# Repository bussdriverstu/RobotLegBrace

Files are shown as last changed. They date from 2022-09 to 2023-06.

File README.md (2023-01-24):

# Robotic Leg Brace
A brace to assist someone with partial paralysis to bend their knee using off-the-shelf parts. Start with 'LegV2' directory.

## Intro Video:
Video Link (https://www.youtube.com/watch?v=BwBtS2pidzo)  
[click to play](https://www.youtube.com/watch?v=BwBtS2pidzo)

## FAQs
### What plans do you have in the future for this project?
~~I have some ideas for reintegrating the muscle sensors back into the leg to have more accurate bend timings.~~ UPDATE: Muscle sensors have been reintegrated, special thanks to [ANR Corp](https://www.anrcorp.com/) for their muscle sensors. I'd also like to program different gait modes for different terrain (hiking, uneven ground, etc).

### How long did this take?
I started the fall of 2021 after being ghosted by a company in San Franscico that makes warehouse exoskeletons. They wanted to expand into the medical field and I volunteered to be a guinea pig. After a few conversations with the CEO I never heard from them again. I assume I lived too far away to make this feasible and they found better candidates. It took me a few months before I started testing it on myself, a little over a year to get it to the point where I could hike with it.

### What is your injury and why is it so difficult to find a therapy?
I had a tumor in my spinal cord. Because it wasn't the result of a tramatic injury, therapies like stem cells are riskier for me. I assume this is because they'd rather avoid growing another tumor, but I don't know. In addition, most robot knee assist devices out there target people who can't hold their weight with their leg, i.e. they can bend but can not straighten their leg. e.g. [The C Brace is one of these devices that I had a consultation with.](https://www.ottobock.com/en-us/c-brace). I have the opposite problem and haven't been able to find a solution so far. After years of frustration, I just decided to try to build my own.

### Why don't you patent this or sell it?
I believe in universal healthcare and have suffered from the ill-effects of for-profit healthcare for a long time. Anyone who has fought with insurance knows the phrase "medically necessary" all too well. Maybe I'm bitter, but I'd rather help people like me for free than join the profit model. Besides, this thing is jank; No one should build it let alone buy it. It works for me and that's good enough. I posted it here in case anyone out there wants to improve it or adapt it for their own needs. That said, you can donate to me or buy me a cup of coffee via bitcoin/ethereum here:  
Bitcoin Address: 36wiXyfY1boAd6eBREEssyqCdySTDvTCo1   
Ethereum Address: 0xE7dC5e4DE2950B2e13B2A2148E09333C0acBa920

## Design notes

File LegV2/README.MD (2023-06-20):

# Robot Leg Brace v2
## Introduction/Warning

Hi. I’ve been handicapped for about 9 years now, I’ve tried to seek out treatments to be able to walk again. However, because of the type of injury and the specific motion I’ve regained, there aren’t many options out there, especially for someone on a fixed income. I took it upon myself to build my own solution. I am not an engineer nor am I a programmer. **I do not recommend anyone follow in my footsteps. THIS IS DANGEROUS.** You could blow yourself up or injure yourself doing what I did. That said, I can walk without my crutch or cane again, which is all I wanted to do. I figured I’d share my project in case anyone else, who is poor and disabled like I am, wants to try to build their own solution. 

## Injury and Ability

My injury is unique and so my solution may not apply to you. I have full motion of my left leg; I can also straighten my right leg out and (mostly) hold my weight with it. The issue I have is being able to bend it back in after pushing it out. I also have foot drop, but I can point my toes easily enough. Again, it’s the bringing my foot back that is the issue. This device will detect when I want to bend my leg and do it for me.

## The Device

The device uses a knee brace as a base. I’ve attached a large servo to the outer thigh portion of the brace and used an old cut-up AFO foot brace to add rigidity to the two sides. I had a friend use a 3D printer to create a pulley to attach to the servo. A chain threaded through a spring which is wrapped around the servo wheel and attaches to the shin portion of the brace via another spring (this is to absorb shock of occasional muscle spasms I can have when my leg moves or is tired). When the servo rotates, it pulls the shin up, bending the knee. 

To control the servo, a microcontroller reads input from various sensors and/or a user-held button and determines when to move, bending or straightening the leg. For example, in Gait/Accelerometer mode, the microcontroller reads data from an accelerometer to determine where my leg is positioned during the walking gait. When the user's thigh reaches a certain angle, it will tell the servo to move, bending my leg. As the user moves forward, the angle will change and the servo will reverse direction, straighten the leg again. See the "Operations" section for more details and controls.

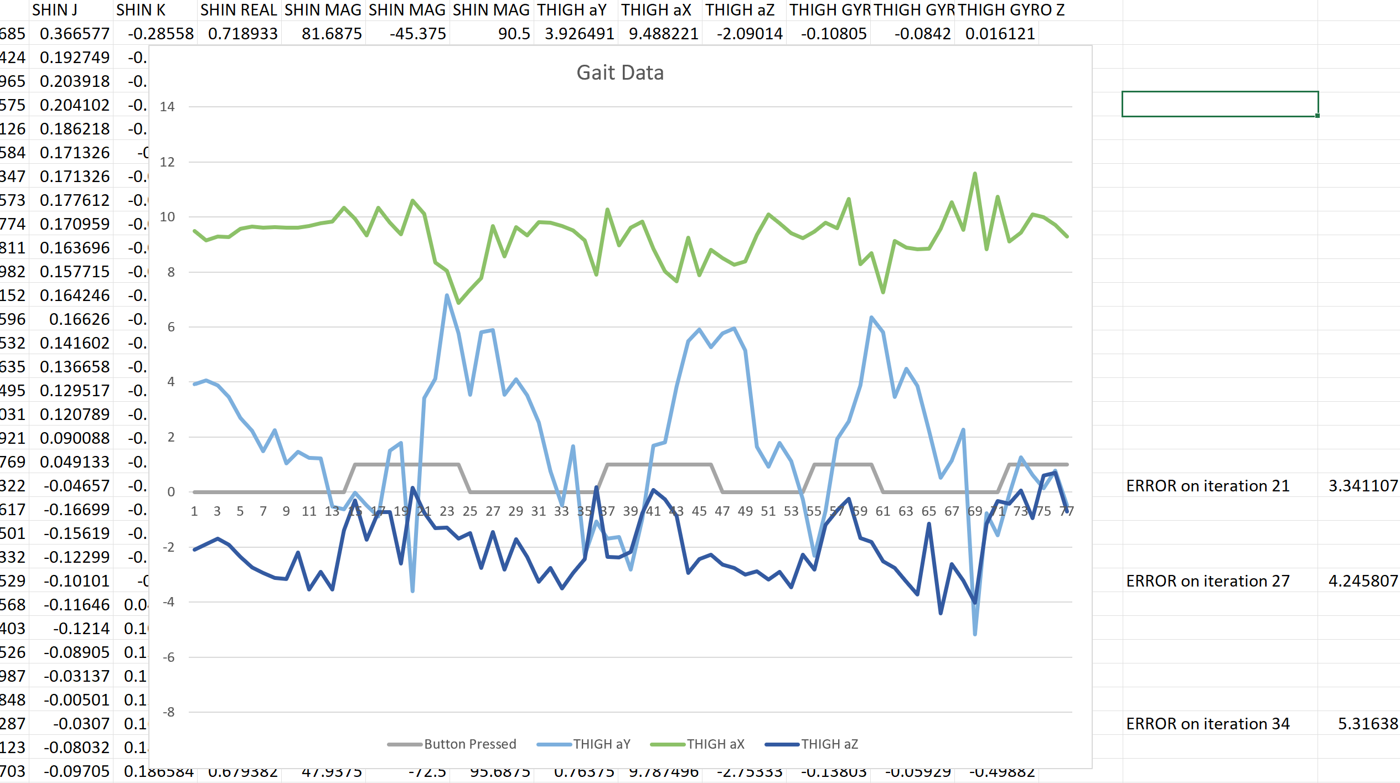
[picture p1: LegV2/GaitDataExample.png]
Gait Data


## Operation

There are a few controls to operate the device. A slider, a hand-held button, and the microcontroller's on-board button. Each have different functions depending on what operating mode the device is in.

### Manual Mode

When the potentiometer slider is at the zero-position (which side that is depends on how you've mounted it) press the handheld button to bend the knee, release to straighten it. When your leg is straight, the on-board LED will be green.

### Gait/Accelerometer Mode

In gait detection mode, the potentiometer slider will set the angle-position threshold that tells the servo when in the walking gait to begin bending the leg and when to straighten it again. A handheld momentary push button is used to override the sensors and manually bend the leg brace. This is useful for steps or uneven ground. You can operate the device in full manual mode by moving the slider all the way to one side (which side depends on how you’ve mounted it, but it will be refered to as the zero-position). An on-board LED light provides visual feedback of what state the brace is in. Green means the leg should be straight, red means the knee should be bent. 

### Muscle Activity Mode

There is an on-board button that will toggle operation from using the brace's position to bend to the muscle sensor. When using the muscle sensor, the light will change from green to blue and the position of the device will not affect bending and straightening. Flexing of the muscle the sensor is positioned on will bend the knee relative to how hard to flex. The slider adjusts the sensitivity of the muscle sensor so that you can get a strong signal from weak muscles. The manual bending button has also been reversed so that when you press it the leg will straighten. This was done as a safety precaution in case interference causes the muscle sensor to report higher readings than the muscle is sending. At rest, the on-board LED will be blue instead of green.

### Hybrid Mode

This mode allows for muscle activity to control the knee only when the leg is positioned within a certain threshold. When enabled it will force the leg to straighten when the leg swings forward past the set threshold. To enable, set the device in Manaul Mode by moving slider all the way to the zero-position in Gait Mode (On-board LED should be green) and use the bend-button to walk. The program will record the position of your leg when you first let go of the button to straighten during each step. Then, switch to muscle activity mode (On-board LED will be blue) and it will straighten your leg at the same position you released the button during the previous step, regardless of the muscle activity registered. To disable this feature, go to Gait mode (press the on-board button so the on-board LED is green and move the slider to any position other than zero) then press and release the bend button again. A white flash will indicate when you have enabled and set, or disabled the setting successfully.

## Installation, Code and Libraries

The code is written in CircuitPython 7.3 and uses the following libraries in the lib folder:

- adafruit_bno08x
- adafruit_bus_device
- adafruit_motor
- adafruit_seesaw
- adafruit_pixelbuf.mpy
- neopixel.mpy

Instructions for installing CircuitPython on the microcontroller can be found here: https://learn.adafruit.com/welcome-to-circuitpython/installing-circuitpython 

After installing, you should be able to copy 'code.py' and the entire 'lib' folder from this repository into the root directory of the microcontroller and you'll be done. Again, I am not a programmer, but I commented what most of it does to the best of my ability. 

## Design/Wiring Diagram

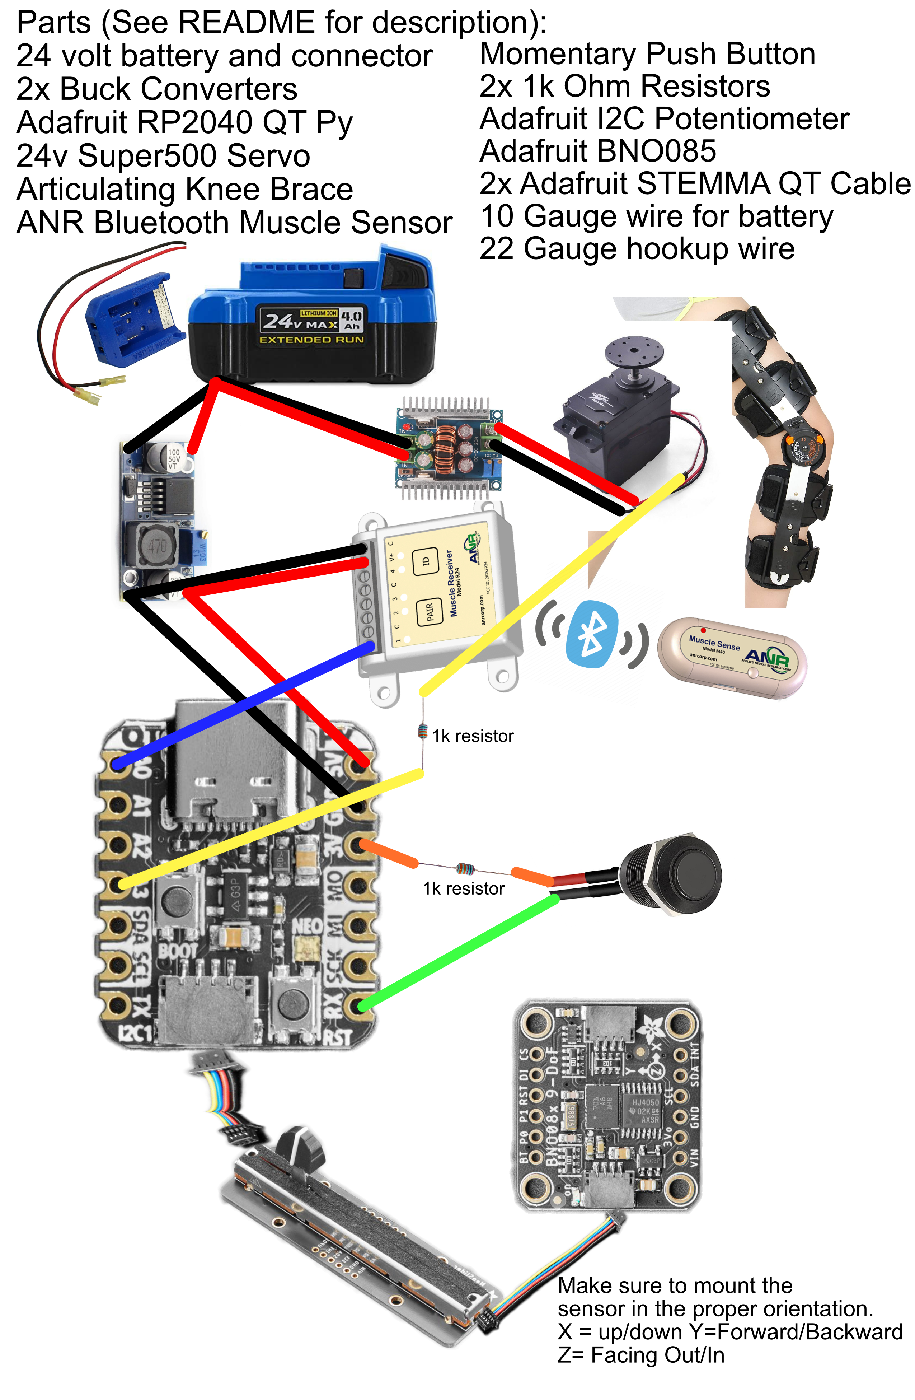
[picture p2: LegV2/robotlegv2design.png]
LegV2 Diagram


## Materials List for building Robot Leg Brace Version 2

- Brace https://www.amazon.com/gp/product/B07BT59Q6X
- Battery https://www.amazon.com/24-VOLT-4-0-AMP-LITHIUM-KB-424-03/dp/B01KAL4IO2
- Battery Quick Connect Terminal Adapter https://www.amazon.com/gp/product/B09BKGX81V
- Small Buck Converter https://www.amazon.com/gp/product/B07MKQXNWG/
- Large Buck Converter https://www.amazon.com/dp/B08GCX2RJ1
- Servo https://www.ebay.com/itm/123414770402
- 10 Gauge Wire https://www.amazon.com/Copper-American-Gauge-Wire/dp/B0796JJHTQ/
- 22 Gauge Wire https://www.amazon.com/Gauge-Wire-Solid-Hookup-Wires/dp/B088KQFHV7/
- Adafruit QT Py RP2040 https://www.adafruit.com/product/4900
- Adafruit BNO085 9-DOF Orientation Sensor https://www.adafruit.com/product/4754
- STEMMA QT Cable https://www.adafruit.com/product/4399
- 1k Ohm Resistors https://www.amazon.com/MCIGICM-Values-Resistor-Assortment-Resistors/dp/B06WRQS97C/
- ANR Corp R24 Muscle Receiver https://www.anrcorp.com/product/r24-muscle-receiver/
- ANR Corp Wireless Muscle Sensor M40 https://www.anrcorp.com/product/m40-muscle-sense/

## Notes

The original design used a Raspberry Pi Zero, input/output controls, a screen, and muscle sensors. It was written in Python 3.7 using multiple libraries from adafruit, waveshare, and users on github. I will upload that version at some point as it was useful for gathering data in my walking gait and experimenting with different techniques for detecting when to bend the leg brace. For now, this is a simplified version targeted toward walking on even ground and can be built with minimal soldering and programming experience.

Once you have the device working, the next challenge will be to fit it on your leg without it moving around. A tight, secure fit is needed to ensure the brace moves your leg instead of moving *on* your leg. I attached the lower portion of the brace directly to my foot drop AFO but still have trouble with the thigh piece sliding around. You will have to experiment on your own to get it right. Good luck.

## Update 2023

Thanks to [ANR Corp](https://www.anrcorp.com/) sending me their muscle sensors and design help from their president, I was able to succesfully integrate muscle sensors into the latest design of the robotic leg. See the operation section for more information on how they operate. ~~I may experiement with more than one muscle sensor in the future.~~ I've started using two sensors, one on the good leg and one on the disabled one. This gives a better picture of my gait so that the brace can respond appropriately. How a short demo of the muscle sensor, watch this video: [https://youtu.be/r48ZZ4WN5bA](https://youtu.be/r48ZZ4WN5bA)

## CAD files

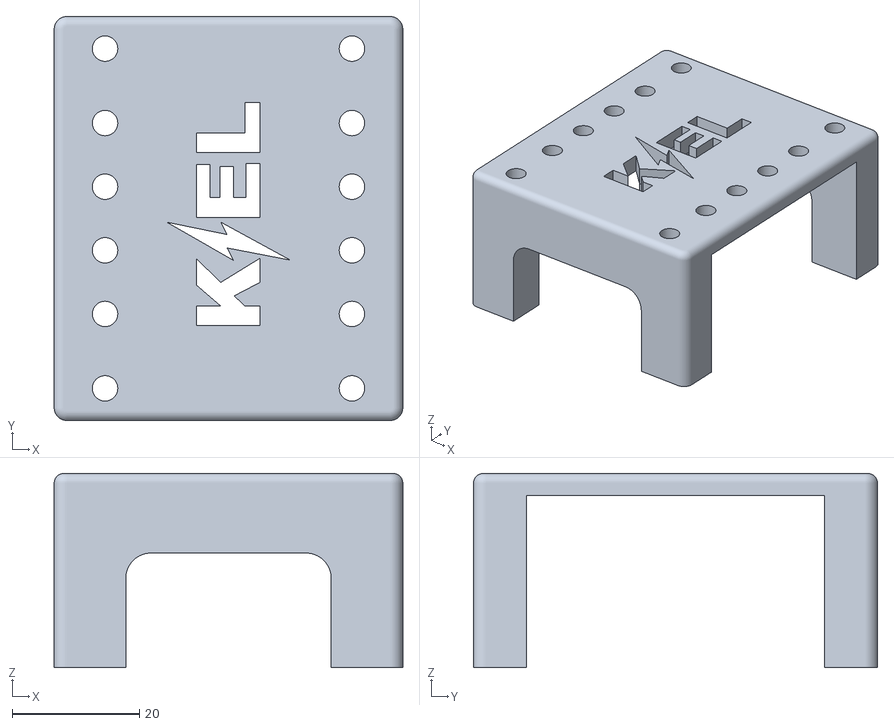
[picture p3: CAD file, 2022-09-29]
3D Printed Parts Files/power-convert-case-top.stl
54.8 x 63.5 x 30.5

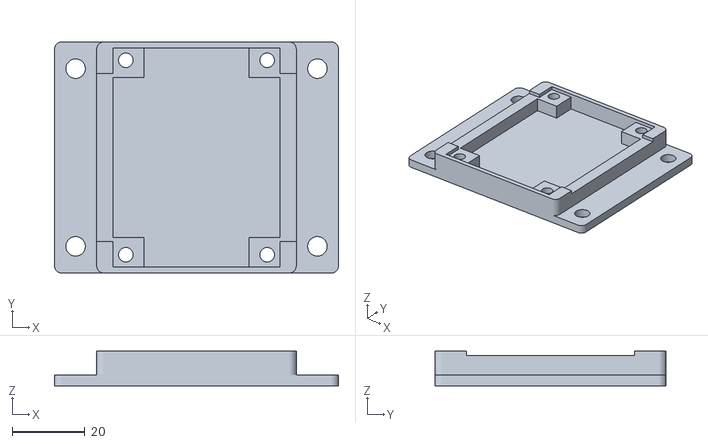
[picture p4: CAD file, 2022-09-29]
3D Printed Parts Files/power-convert-case-btm.stl
78.0 x 63.5 x 9.50

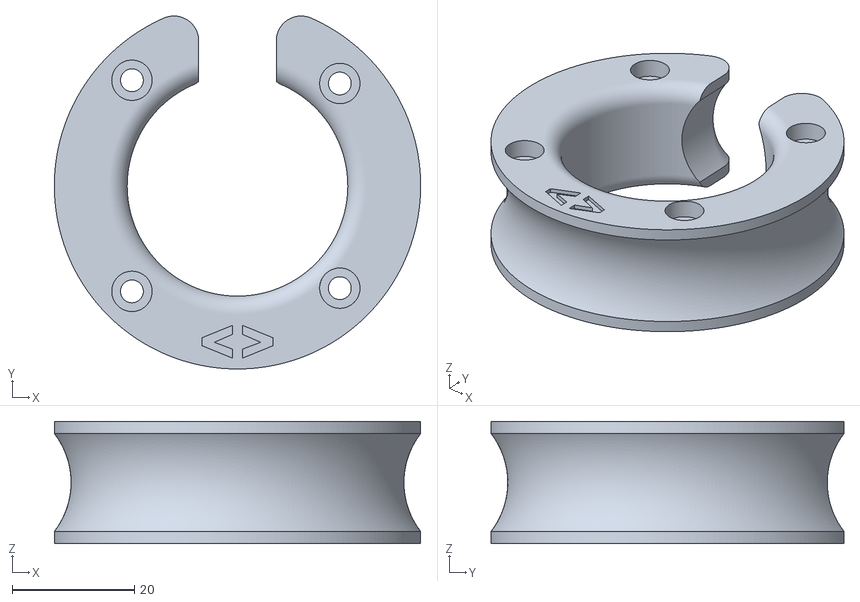
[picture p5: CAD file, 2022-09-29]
3D Printed Parts Files/spring-guide.stl
60.0 x 57.8 x 20.0

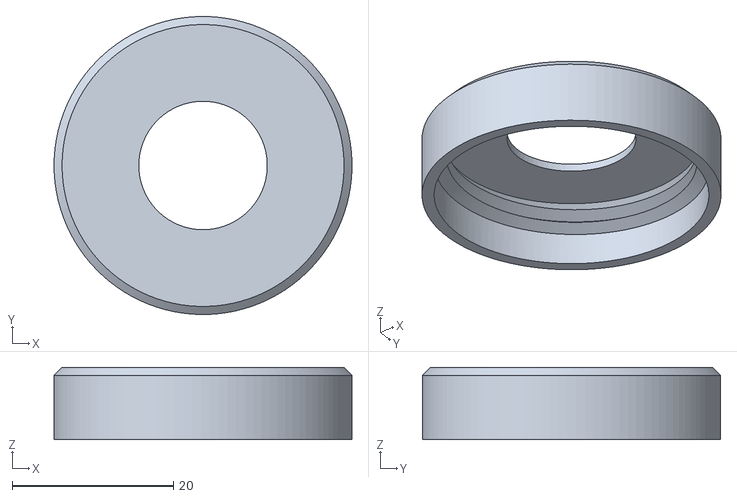
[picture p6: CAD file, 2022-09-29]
3D Printed Parts Files/button-top.stl
37.0 x 37.0 x 9.00

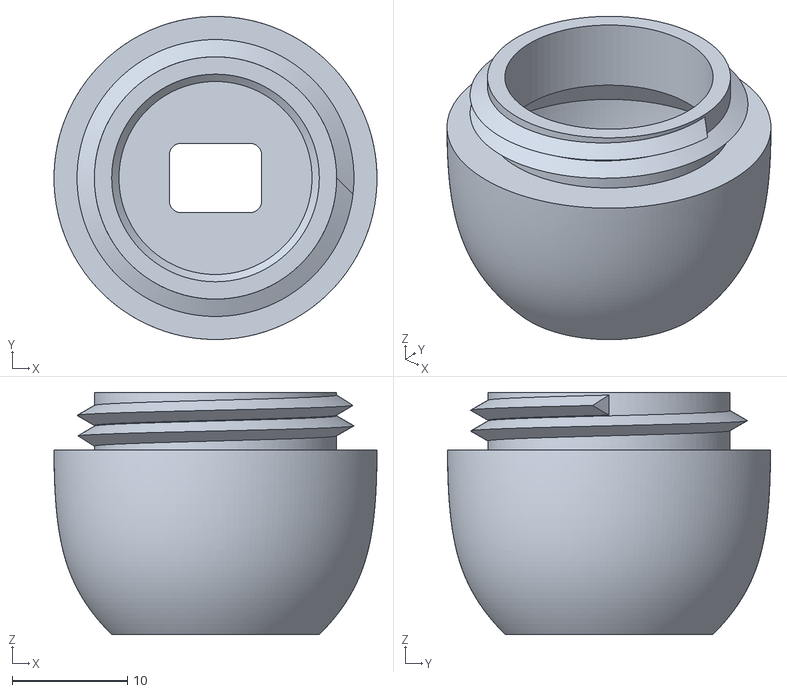
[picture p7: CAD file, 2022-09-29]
3D Printed Parts Files/button-btm.stl
28.0 x 28.0 x 21.0

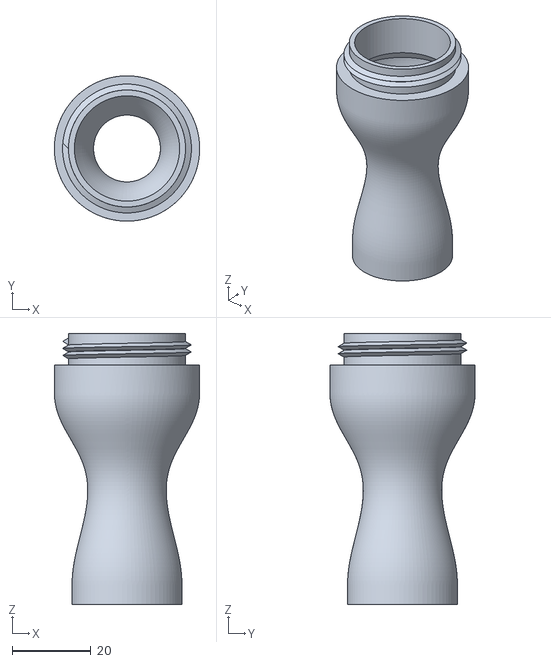
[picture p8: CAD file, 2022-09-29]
3D Printed Parts Files/button-mid.stl
37.0 x 37.0 x 69.0

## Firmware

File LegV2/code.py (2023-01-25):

import time
import board
import neopixel as boardpixel
from rainbowio import colorwheel
from adafruit_seesaw.seesaw import Seesaw
from adafruit_seesaw.analoginput import AnalogInput
from adafruit_seesaw import neopixel
from adafruit_bno08x import BNO_REPORT_ACCELEROMETER
from adafruit_bno08x.i2c import BNO08X_I2C
import pwmio
from adafruit_motor import servo
import digitalio
from analogio import AnalogIn

# Calibration mode (This is for using both the muscle sensor and accelerometer do provide optimal straightening timing)
calibratedThreshold = None

# Muscle Sensor Configuration
usingMuscleSensor = False
analogPinA0 = AnalogIn(board.A0) # Use on handicapped leg
analogPinA1 = AnalogIn(board.A1) # Use on strong leg

# Button for brightness control of on-board LED
boardButton = digitalio.DigitalInOut(board.BUTTON)
boardButton.switch_to_input(pull=digitalio.Pull.UP)
ledBrightness = 0.01

# Bend Button
button = digitalio.DigitalInOut(board.RX)
button.switch_to_input(pull=digitalio.Pull.DOWN)

# On Board Pixel
onBoardPixels = boardpixel.NeoPixel(board.NEOPIXEL, 1)

# NeoSlider Setup
neoslider = Seesaw(board.STEMMA_I2C(), 0x30)
potentiometer = AnalogInput(neoslider, 18)
pixels = neopixel.NeoPixel(neoslider, 14, 4, pixel_order=neopixel.GRB)

# Positional Sensor
bno = BNO08X_I2C(board.STEMMA_I2C())
bno.enable_feature(BNO_REPORT_ACCELEROMETER)

# Servo things
pwm = pwmio.PWMOut(board.A3, frequency=50)
servo = servo.Servo(pwm)
up = 1
down = 120
lastValue = 120

def DoCalibration(threshold):
    global calibratedThreshold
    if (calibratedThreshold == None or threshold == None):
        calibratedThreshold = threshold
        print(calibratedThreshold)
    onBoardPixels.fill((255, 255, 255))
    pixels.fill(0)

def PotentiometerToThreshold(value):
    return (-1 * ((value / 1023 * 6.0) - 2)) # Number multiplied is range, number subtracted determines higher bound, -1 is there to flip the slider motion to match the muscle sensor sensitivity operation. In this case, the range goes from -4 to 2.

def PotentiometerToRange(value):
    return (value / 1023 * 4) + 1 # Number multiplied is range, number added determines lower bound. In this case, slider returns values between 1 and 5.

def PotentiometerToColor(value):
    return value / 1023 * 255 # Scale the potentiometer values (0-1023) to the colorwheel values (0-255)

def ControlLightsBasedOnServoPosition(position): # Controls LEDs based on servo position
    if (usingMuscleSensor): # Some code to control led brightness and color for visual feedback
        ratio = position / 120
        ledBrightness = int(255 - (254 * ratio)) # Changes brightness of on-board LED based on muscle activity
        #print("Ratio: " + str(ratio))
        pixels.fill(0)
        colorBrightness = colorwheel((int(165 * ratio)) & 255) # Colors blue to red on color wheel
        ledCount = 4 # Number of LEDs is slider strip
        for i in range(ledCount): # Cycle through LEDs 
            threshold = (ledCount-i)/ledCount # Spits out evenly spaced thresholds based on number of LEDs to compare to the ratio. In this case, 4 LEDs spit out 1, 0.75, 0.5, and 0.25
            if (ratio < threshold): # If muscle activity is within a certain threshold...
                pixels[i] = colorBrightness # Assign color and brightness
    else:
        pixels.fill(colorwheel(PotentiometerToColor(potentiometer.value))) # Changes led colors on slider based on the position of the potentiometer.
        ledBrightness = 1
    if (position <= lastValue and position < 120): # Determines when leg is bending vs straightening and not at rest straightened.
        onBoardPixels.fill((ledBrightness, 0, 1)) # On-board led turns red when bending, brightness determined by how bent the knee is (if using muscle sensor)
    else:
        onBoardPixels.fill((0, 0, ledBrightness)) # When straight, on-board led turns green if using positional sensor or blue when using muscle sensor, brightness determined by how straight the knee is (if using muscle sensor)
    
def SendSignal(position):
    global lastValue
    ControlLightsBasedOnServoPosition(position) # Update LED colors and brightness
    if (position != lastValue): # Checks the last sent signal so duplicate signals aren't sent every loop. Not sure if it matters... ¯\_(ツ)_/¯
        servo.angle = position
        lastValue = position
        #print("Signal Sent")

def ChangeMode():
    global usingMuscleSensor
    if (usingMuscleSensor):
        usingMuscleSensor = False
    else:
        usingMuscleSensor = True
    time.sleep(.3) # Cheap debounce

def ChangeBrightness(): # This function is no longer called anywhere, but I may integrate it back in at a later date. # ChangeBrightness() # If the on-board button is pressed, it will change the brightness multiplier for on-board LED. Values are off, dim, medium, bright.
    global ledBrightness
    if (ledBrightness == 0.0): # This modifies the value of ledBrightness which is then used as a multiplier for brightness. 0 = off, .01 = 10%, .5 = 50%, 1 = 100%
        ledBrightness = 0.01
    elif (ledBrightness == 0.01):
        ledBrightness = 0.32
    elif (ledBrightness == 0.32):
        ledBrightness = 1.0
    else:
        ledBrightness = 0.0

def GetVoltage(pin):
    return (pin.value / 65536) # Returns percentage of 16-bit max-value of muscle sensor.

servo.angle = down # Start leg in straight position on boot

while True:
    try:
        accel_x, accel_y, accel_z = bno.acceleration # Gets position of thigh
        if not boardButton.value: # If on board button is pressed, changes mode from accelerometer controlled to muscle sensor controlled
                ChangeMode()
        if (usingMuscleSensor):
            muscleOneReading = GetVoltage(analogPinA0) # Muscle Sensor One
            muscleTwoReading = GetVoltage(analogPinA1) # Muscle Sensor Two
            rangeAdjustment = PotentiometerToRange(potentiometer.value)
            #print("Actual Voltage %: "+str(muscleOneReading) + ", Range Multiplier: " + str(rangeAdjustment))
            if (muscleOneReading < .04): # Ignore small muscle activity like weak twitches
                muscleOneReading = 0
            mappedRangeValue = int(muscleOneReading * -120 * rangeAdjustment) + 120  # Maps range of muscle activity to range of servo and determines servo value to send. Servo Position = (Muscle Sensor 0-1 * Range as a negative because higher values mean straight while lower means bend * increases the range so servo is more sensitive to activity) + our starting point of the range so that 0 muscle activity means servo position is at 120, which is down.
            if (mappedRangeValue < 1): # When sensitivity slider is set higher than 0, it's easy to go beyond the max limit for the knee to be bent. This keeps it in bounds.
                mappedRangeValue = 1
            if (mappedRangeValue > 120): # Same here, but on the other extreme. If I did my math right it should never go higher than 120 anyway.
                mappedRangeValue = 120
            #print("Adjusted Voltage %: "+str(muscleOneReading) + ", Signal to Send: " + str(mappedRangeValue))
            if (button.value): # Button acts as a safety switch, pressing it will tell the servo to keep the knee straight
                SendSignal(down) # This value will always be 120.
                print("Adjusted Voltage %: "+str(muscleOneReading) + ", Signal to Send: " + str(mappedRangeValue))
                print("X: %0.6f  Y THRESHOLD VALUE: %0.6f Z: %0.6f  m/s^2" % (accel_x, accel_y, accel_z)) # Will use these values you determine when to ignore muscle sensor activity and just straighten the leg
            else:
                if (calibratedThreshold is None or accel_y > calibratedThreshold): # If using the accelerometer in muscle mode, straighten leg past the calibrated threshold
                    SendSignal(mappedRangeValue) # this value will be somewhere between 120 and 1. 1 is knee completely bent, 120 is completely straight.
                else:
                    SendSignal(down)
                print("calibrated: "+str(calibratedThreshold))
                print(accel_y)
        else:
            threshold = PotentiometerToThreshold(potentiometer.value)
            print("Threshold: " + str(threshold))
            print("X: %0.6f  Y: %0.6f Z: %0.6f  m/s^2" % (accel_x, accel_y, accel_z))
            if (accel_z > -4 and accel_z < 4): # Checking to make sure the leg is upright in case user has fallen over
                if (accel_y > threshold or button.value): # Checks if the accelerometer reading is greater than the threshold set by the slider position or if the button is pressed, then bends the leg if either are true.
                    print("bend")
                    SendSignal(up)
                    onBoardPixels.fill((255 * ledBrightness, 0, 0)) # On board led turns red when bending, brightness determined by on-board button
                else: # Straightens the leg
                    print("straight")
                    if (lastValue is not down): # fire this once at the moment the button is released
                        if (threshold == 2): # If slider is all the way at 2 (i.e. full manual mode)...
                            DoCalibration(accel_y) # Take note the instance the leg straightens and assign muscle sensor straighten threshold for muscle activity mode
                        else:
                            DoCalibration(None) # If the slider is not at 2, assign None to calibration to ignore position sensor in muscle activity mode
                    SendSignal(down)
                    onBoardPixels.fill((0, 255 * ledBrightness, 0)) # On board led turns green when straight, brightness determined by on-board button
            else:
                print("you fell over, clumsy nerd")
    except Exception as e:
        print("An error has occured, likely a misread from a sensor and can be ignored. Error: "+str(e))
    #time.sleep(.2) # I use this for debugging to read all my print statements. Remove it when using in production.

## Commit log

2022-09-11 Initial Commit of Version 2
    Version 2 of the robotic leg brace. Uses Adafruit CircuitPython 7.3.1 and Adafruit QT Py RP2040 with rp2040 chip.
2022-09-27 Update code.py
    Added brightness control for on-board LED via on-board button.
2022-09-27 Create MaterialsList.MD
    List of materials with links to purchase
2022-09-27 Delete MaterialsList.MD
    List is now in readme.md
2022-09-27 Design/Wiring Diagram
2022-09-29 Add files via upload
    3D Printer files for servo mounting
    [button-btm.stl, button-mid.stl, button-top.stl, power-convert-case-btm.stl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]
2023-01-12 Update code.py
    Added support for a muscle sensor using analog pin 0 on the board. On-board button switches between positional sensor control mode and muscle sensor control mode.
2023-01-12 Update README.MD
    Updated operations section to include newly integrated muscle sensor mode.
2023-01-18 Update code.py
    Added sensitivity control to muscle sensor mode via slider and updated LED visual feedback.
2023-01-20 Update code.py
    Updated and extracted LED control code from sendSignal function.
2023-01-21 Update README.MD
    Added muscle sensor materials. Muscle sensor graciously provided by ANR Corporation.
2023-01-22 Update README.MD
    Updated operating instructions to detail switching modes and calibrating sensors.
2023-06-20 Update README.MD
    Added muscle sensor video to 2023 update
